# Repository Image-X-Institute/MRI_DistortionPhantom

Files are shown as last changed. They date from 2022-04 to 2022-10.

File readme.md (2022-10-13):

# MRI_DistortionPhantom


> :warning: this repo is archived; the most up to date documentaiton and code can be found [here](https://github.com/ACRF-Image-X-Institute/mri_distortion_toolkit)

This repository contains code to generate a customized MRI Distortion Phantom in [FreeCAD](https://www.freecadweb.org/). We also provide a 'how to' on manufacturing and imaging such a phantom in [our documentation](https://acrf-image-x-institute.github.io/MRI_DistortionPhantom/). For analysis of the phantom images, please see [this repository](https://github.com/ACRF-Image-X-Institute/MRI_DistortionQA)

Compared to other MRI distortion phantoms, this is:

- Free and open source
- Completely user customizable  
- Water free: light weight and leak free
- Designed for cheap and easy construction



## Setup/Build/Install

- Download and install [FreeCAD](https://www.freecadweb.org/). This work was tested with FreeCAD V0.19. The scripts will be executed within the FreeCAD python environment, so you don't need any additional libraries.
- Clone this repository

## Usage

- To generate your first phantom design, please see the [getting started](https://acrf-image-x-institute.github.io/MRI_DistortionPhantom/GettingStarted.html) page in the docs
- Important note: This code is <u>only</u> designed to worked from within FreeCAD. Any attempts to execute it from outside FreeCAD will fail.

## Directory Structure

- **docs** contains html documentation
- **docsrc** markdown/rst source documentation

## Acknowledgements 

This phantom design draws heavily on previous work undertaken at Ingham Institute/ Liverpool Cancer Center on MRI phantom development as described [here](https://aapm.onlinelibrary.wiley.com/doi/pdfdirect/10.1118/1.4915920?casa_token=CcBf93ylYfoAAAAA:yn6h_k-mTRJ2orijpwzfoUtX5zZchs-_qbcifwIP8X6oX2K19QKc7g7_oMXPMyspkzFAdUe-7rqEavzHzQ).

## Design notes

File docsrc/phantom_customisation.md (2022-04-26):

# Phantom Customization

The baseline model of a distortion phantom is highly customizable. You can change any of the parameters in the FoamProtoypeExample.py file. One of main reasons you may wish to do this is that different scanner have different field of views, so you may wish to make your phantom larger or smaller.
All options for the AddPhantomSlice class are described within the [code docs](), but we provide some additional notes on some of the more common things you may wish to change below:

## Specifying marker locations 

The marker locations are specified on each slice object. We provide two methods to automatically generate marker locations: ```HoleCentroids=cartesian``` will generate a cartesian grid of markers, while ```ROI_polar```  will generate concentric rings of markers. Both wil the ```hole_spacing``` parameter to space out markers. If you specify a ```DSV```,  the ```ROI_polar``` option will ensure good marker coverage over the surface of this sphere, and will provide an etch of the intersection of the DSV on each slice surface so you can tell where the DSV is on each slice.

You can specify a crosshair of markers using the ```ReferenceCrosshairRadius``` option. This will add a crosshair of markers within ```ReferenceCrosshairRadius```. This is a good idea to add to the central slice, as it makes alignment with CT/Ground truth much easier.

Finally, you may not wish to use any of the existing methods for defining marker positions. In that case, you are free to simply specify them as a list: ```HoleCentroids = [[x1,x2,x3],[y1,y2,y3]]```

## Specifying a load region

This phantom consists of a base material that does not give MRI signal, and is then packed with oil capsules, which also don't generate much signal. This can result in the RF coil of the scanner not being properly loaded. To avoid this, it is a good idea to add some load to your phantom. You can specify a region to be cut from the center of each slice using e.g. ```LoadRegion={'shape': 'rectangle', 'width': 100, 'height': 200}``` (see code docs for other options).

In our experience, not much load is required: during development we simple put a container of oil capsules into a zip lock bag. The exact location of the load also shouldn't be especially sensitive, just put it somewhere near the middle. 

## Specifying a DSV

Specifying a Diameter of Spherical Volume (DSV) has two effects

1. the intersection of the DSV with each slice will be etched on the surface of the slice
2. If you specify ```HoleCentroids=ROI_polar``` then the code will ensure good marker coverage over the surface of the DSV sphere. This can be important if you wish to fit spherical harmonics using this data.

## Specifying Guide Rods

This phantom is based on the concept of individual slices which are stacked on top of each other. A number of methods can be envisaged to hold all of these slices together, but internally we have been using nylon guide rods with great success. 

To specify guide rods, simply use ```GuideRods={'radius': 5, 'position': 30, 'height': 370}```. This will add four holes to the corner of your slice. Each hole will have a radius of` radius` and be  `position` mm from the edge of the slice.

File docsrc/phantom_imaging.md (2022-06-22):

# Phantom Imaging

Below are some things to think about when imaging the phantom. \

All our development work has been on a siemens scanner running VB 19A. Therefore, although the principles outlined below are scanner independent, the specific instructions are siemens specific. If you can update these instructions for other vendors, please do so! 

## Fat-Water chemical shift
If you use oil capsules as the markers in your phantom, there is an important effect you must be aware of: [Fat-Water chemical shift](https://mriquestions.com/f-w-chemical-shift.html). This means if your scanner has a center frequency calibrated for water (which it almost certainly does), the oil based capsules will be offset in the readout direction. There are a number of things you can do to avoid this:

1. **Set the scanner center frequency to oil instead of wate**r. Most scanners should have some method to reset the central frequency based on a given load. Specific instructions are scanner specific; an example from our siemens scanner is shown below.  The phantom itself may not provide sufficient load to carry out this procedure; in this case you could simply use a bottle of oil. If you successfully reset the central frequency, you will remove any offsets due to fat-water shift. The central frequency is encoded in the dicom header, so you can always retrospectively check what was used.
2. **Use a large bandwidth**: Since fundamentally this is a B0 distortion, the same mitigation used for B0 can be used. If you use a large enough bandwidth, the fat-water shift will be almost eliminated. However, this will also result in a drop in SNR, so the tradeoff must be made carefully. 
3. **Correct in software**: the fat-water shift is a known effect; its magnitude at a given field strength can easily be calculated. Therefore, it is in possible to [correct for it in software](https://acrf-image-x-institute.github.io/MRI_DistortionQA/code_docs.html#module-MRI_DistortionQA.MarkerAnalysis).
4. **Use water based markers:** In many ways this is the ideal solution, except for one thing: we haven't been able to find any water based markers yet!

In general, the best way to check whether you have removed the fat-water shift is to compare markers near the **center** of a phantom that were taken with a forward/reverse read out gradient (instructions for a siemens scanner below). Since B0 homogeneity should be good at the center of the phantom, if the central markers are not well aligned then it is because fat-water shift.

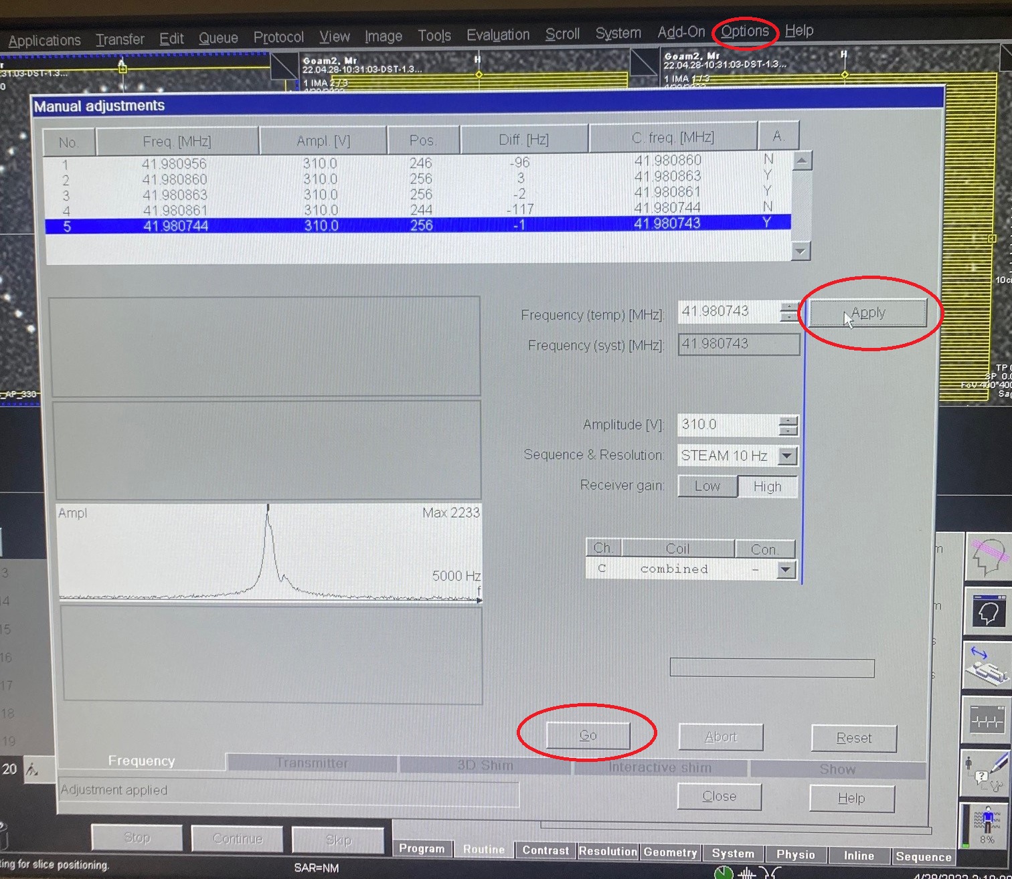
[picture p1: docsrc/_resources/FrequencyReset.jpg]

**Figure: for a siemens scanner, the center frequency can be reset for a given load by going options>>adjustments then clicking go until the measurement converges (may take a few tries). Then click apply to apply the new frequency.**

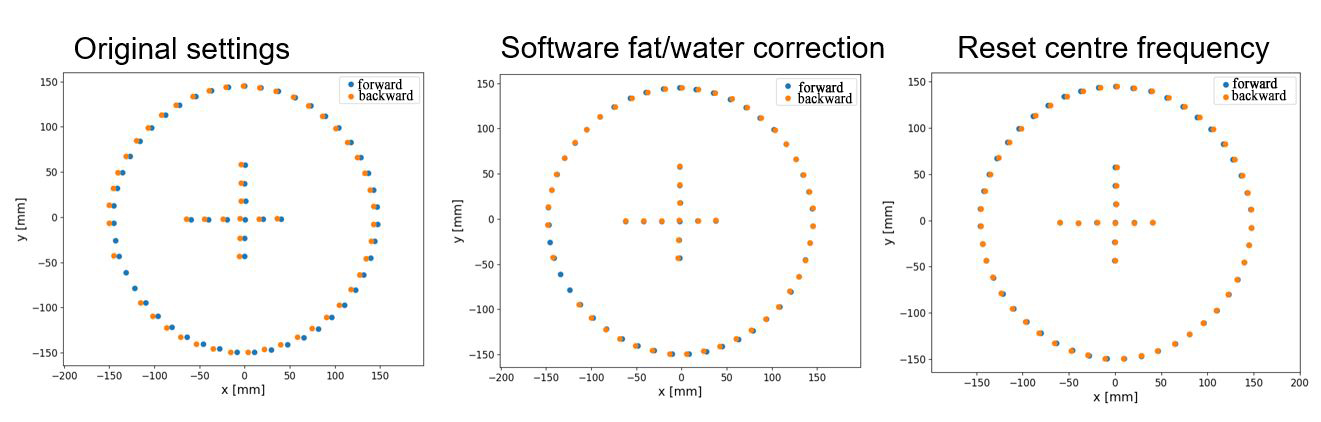
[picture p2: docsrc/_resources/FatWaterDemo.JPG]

**Figure: In the original image, no fat water correction has been made. As a result, the markers in the center of the image are offset from each other in the frequency direction. In the second image, this effect has been corrected for in software. In the third image, this effect has been corrected for by adjust the center frequency of the scanner.**

## Separation of B0/ Gradient distortion effects

There are two 'system based' sources of distortion in MRI: the gradient coils, and B0 inhomogeneity (there are also patient specific effects, which we ignore here.)

- Gradient distortion appears in every direction, and is essentially independent of imaging sequence.
- For standard sequences, B0 distortion appears only in the **readout** (frequency encode) direction, and is [highly sequence dependent](https://pubmed.ncbi.nlm.nih.gov/19810464/) . 

For a given sequence, these effects can be separated as follows: 

1. Take the first phantom image
2. Reverse the phase encoding direction. See image below for example in a siemens scanner.
3. The gradient distortion is the same in both images, while the direction of B0 distortion is reversed. Therefore, the gradient distortion is the average position of each marker between the two images.

To put this into a very simple example: consider just one marker and one dimension. This marker has a ground truth position (for instance measured with CT) of x_gt; gradient non-linearity causes it instead to appear at x_gnl. If we take two scans with opposite encoding directions x_forward and x_backward, we observe this marker at x_scan1 and x_scan2. We can separate the gradient and B0 effects as follows:
```
x_gnl = mean(x_scan1, x_scan2) = (x_scan1, x_scan2)/2
x_b0 = x_gt - x_gnl
```
At this point, we have a good estimate of the perturbation caused by gradient non-linearity in x which will be sequence independent, and a good estimate of the perturbation caused by B0, which will be sequence dependent. We would then have to repeat this process for encoding directions y and z to get a good estimate of each gradient field.

If this all makes your head hurt as much as it does mine, you have two options:

1. If you don't care about B0 (e.g. you are sure it is small enough that you don't need to worry about it), then use a large imaging bandwidth in conjunction with a spin echo sequence. Both of these will minimize your sensitivity to B0 inhomogeneity such that you can ignore B0 effects.
2. We have provide analysis software (**coming soon**!) ADD LINK that automates these steps for you. 

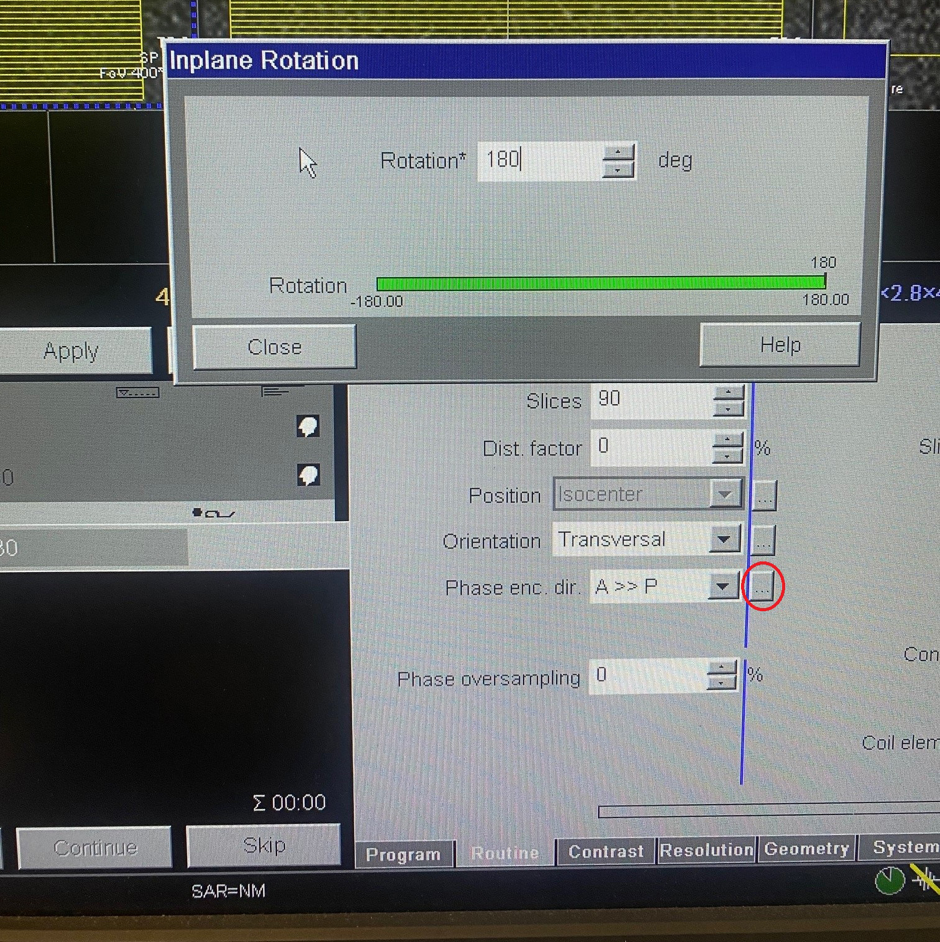
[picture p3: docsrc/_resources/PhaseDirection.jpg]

**Figure: this is the screen where you can reverse the phase encoding direction in the Siemens software. In the siemens software, reversing the phase encoding direction also reverses the read out (frequency) direction.**

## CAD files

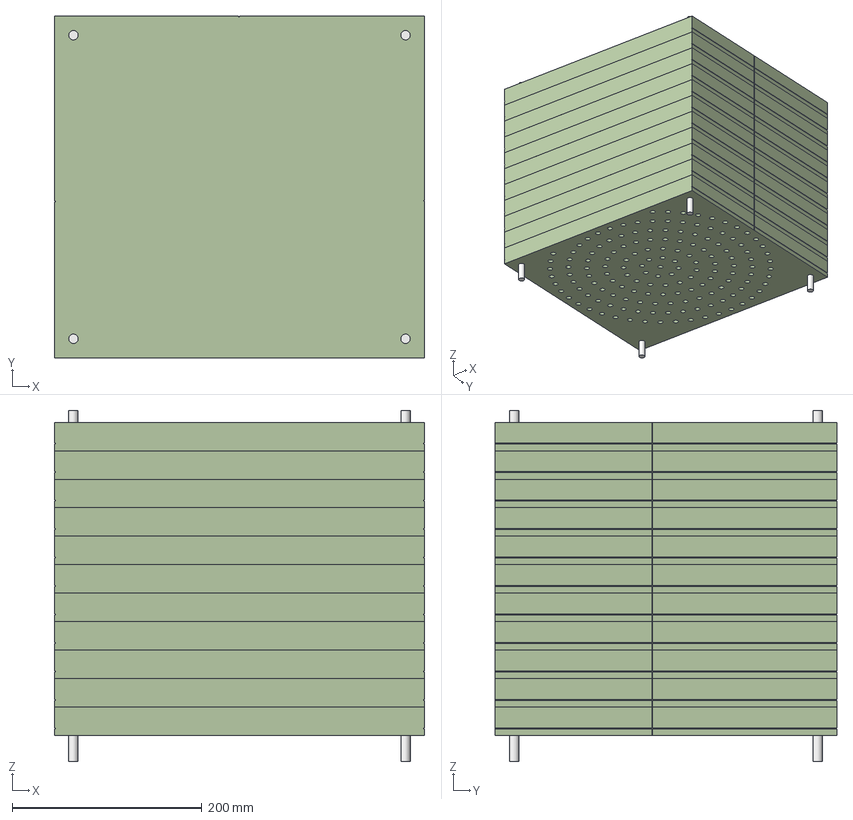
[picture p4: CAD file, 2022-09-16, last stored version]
phantom_drawings/EvolutionGearPhantom.FCStd
390.0 x 360.0 x 370.0 mm
Slice_z__150_0
Slice_z__120_0
Slice_z__90_0
Slice_z__60_0
Slice_z__30_0
Slice_z_0_0
Slice_z_30_0
Slice_z_60_0
Slice_z_90_0
Slice_z_120_0
Slice_z_150_0
DSV
Guide_TL011
Guide_TR011
Guide_BR011
Guide_BL011
combined_guides011

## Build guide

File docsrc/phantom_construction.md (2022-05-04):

# Phantom Construction

To a first order, the intention of this repository is to enable users to generate a CAD model of a distortion phantom; exactly how to construct it and what to construct it from is somewhat up to the user!

With that said, here are some notes about how we have gone about this previously.

## Specifying geometry for manufacture

When you build your phantom, each "Slice" object has a method called ```add_full_scale_drawing```. This does exactly what it sounds like: adds a 1:1 scale drawing of that slice into the FreeCAD object tree. To add a drawing of a slice, the code looks like the below.

````py
Slice = PhantomBuilder.AddPhantomSlice()
Slice.add_full_scale_drawing()
````

In the FoamPrototypeExample we provide, you would have to add the add_full_scale_drawing() call to eace slice in the for loop.

To export each drawing, simply select it, click file, export, then export as pdf.

From here, you can either print out each pdf if you intend to construct a phantom manually, or send this directly to the manufacturer. In our experience, this pdf drawing along with a phone call were all manufacturers needed.

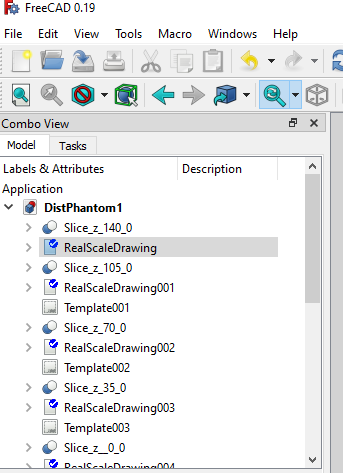
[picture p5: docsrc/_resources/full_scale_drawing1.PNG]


**Figure: using the full_scale_drawing** adds multiple drawings into the Model tree. Each of these must be manually exported (for now. we will add an auto method in future)

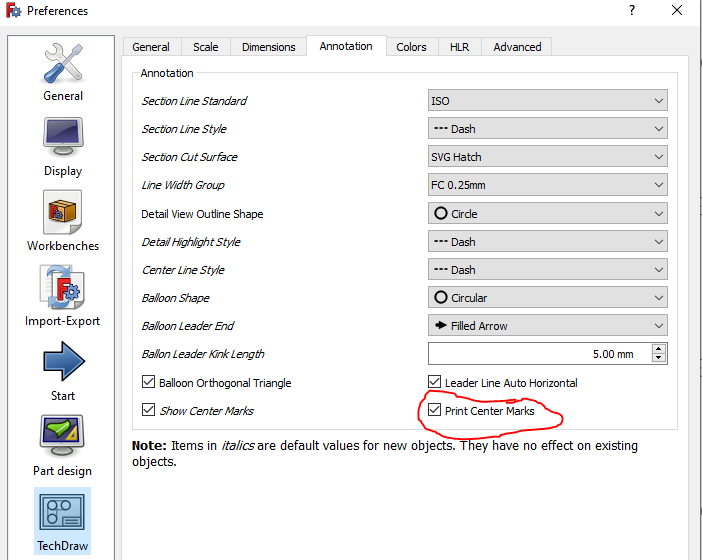
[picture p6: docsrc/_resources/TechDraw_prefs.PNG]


**Figure: we suggest enabling the 'Print Center Marks' option, which doesn't show up in FreeCAD but will print a crosshair in each circle when you export to pdf. This is especially important if you intend to manually drill the holes**

## Markers

The phantom has a number of holes to put markers in, but what should you actually use for markers? We have had a lot of success using fish oil capsules such as [these](https://www.blackmores.com.au/products/fish-oil-1000). Note that the use of oil has ramifications for MRI imaging; we discuss these and provide [suggestions on how to take images safely](https://acrf-image-x-institute.github.io/MRI_DistortionPhantom/phantom_imaging.html)

## Background material

The slice could be constructed of anything MRI neutral. We have constructed phantoms from [blue foam](https://dctech.com.au/products/styrofoam-rtm-x/) and [add type of foam](https://www.evolutiongear.com.au/custom-foam-cutting/). If you can find a robust way to manufacture it, foam is an excellent choice as it is super lightweight and storng. However, as described below it can be difficult to manufacture. Alternatively you could use a lightweight plastic but note that even 'light' plastic tends to get quite heavy!

## Joining the slices together

To join the slices together, we used [threaded nylon guide rods](https://www.unitedfasteners.com.au/products/fasteners-fixings/nylon/threaded-rod/nylon-threaded-rod), [washers](https://www.unitedfasteners.com.au/products/fasteners-fixings/nylon/washers/nylon-flat-round-standard-washer) and [nuts](https://www.unitedfasteners.com.au/products/fasteners-fixings/nylon/nuts/nylon-wing-nut). One could also imagine for instance a specialized 'slice holder' like a box that all the slices could slot into, but we did not explore this. 

## Before your first prototype: general tips

- Getting the holes the right size for the markers can involve some trial and error. It's a good idea to build a few single slice prototypes before continuing to a full design. 

## First prototype: Drill press

For our first phantom, we used a drill press on  [blue foam](https://dctech.com.au/products/styrofoam-rtm-x/). An image of this is below. This was quite sucessful, but rather painful to construct a phantom with many holes drilled. There are also obvious limitations to the accuracy of hole placement. We also found that unless you have a high quality drill press, the foam is quite prone to crumbling. 

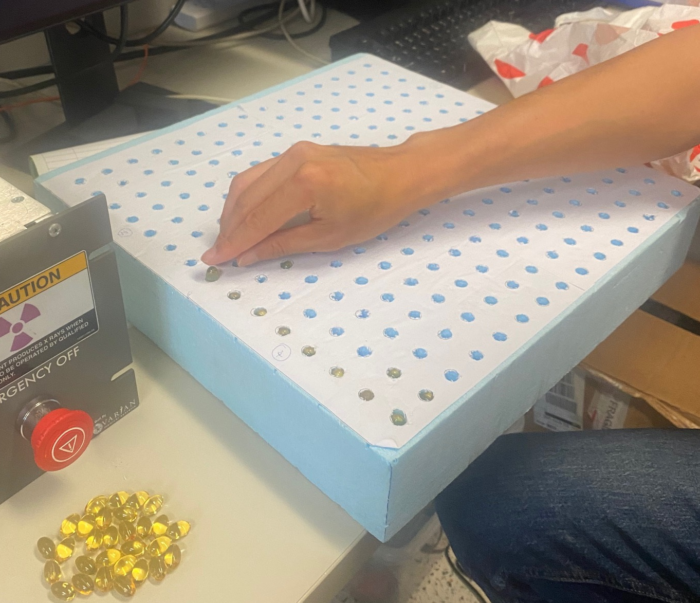
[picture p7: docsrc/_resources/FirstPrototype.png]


**Figure: Action shot of our first slice prototype in action!**

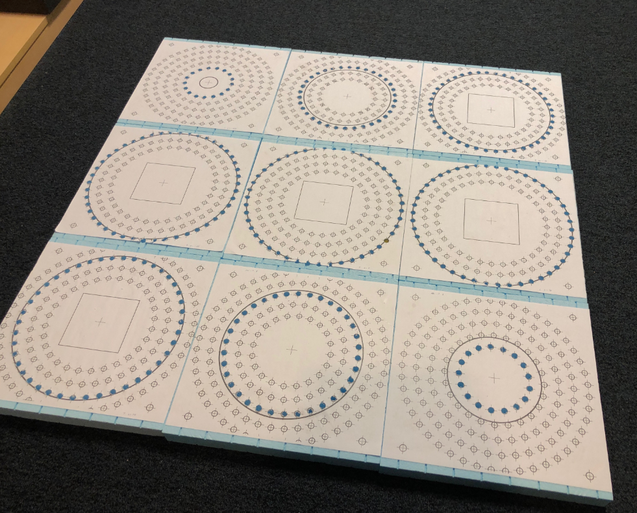
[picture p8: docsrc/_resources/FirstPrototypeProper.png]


**Figure: all slices from a drill press based phantom**

## Second protoype: Laser cut foam

The drill press version was excellent for development, but long term we wanted something more accurate and less labor intensive. For our second prototype, we utilized laser cut foam. There are many vendors capable of this manufacturing technique; we worked with [evolution gear](https://www.evolutiongear.com.au/custom-foam-cutting/). 

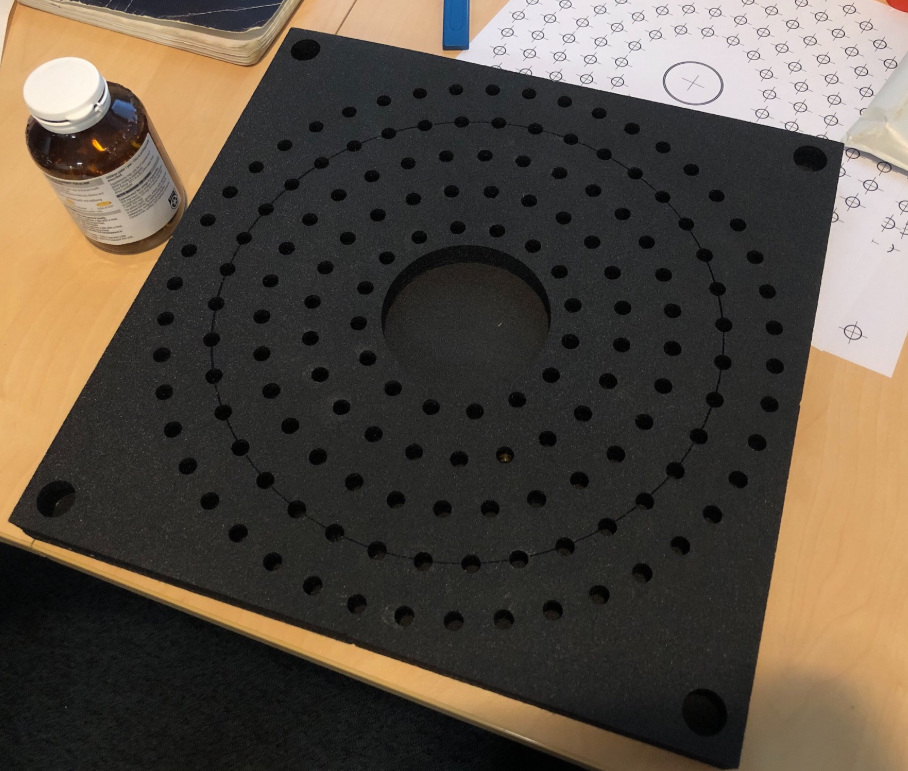
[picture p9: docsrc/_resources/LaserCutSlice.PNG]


**Figure: slice from a laser cut foam provider**

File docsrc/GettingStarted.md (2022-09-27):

# Getting Started

## Setting up FreeCAD

FreeCAD of course has its [own documentation](https://wiki.freecad.org/Getting_started), which should be your first point of call for any trouble shooting of this program. Here, we provide a basic intro into setting up and configuring freeCAD so that you can build your first phantom. 

1. [Download FreeCAD](https://www.freecadweb.org/downloads.php). This code was developed and tested with version 0.19. Future versions should work, but if you run into issues go with version 0.19
2. Open FreeCAD 
3. In “View” “panels” enable both the python console and the report view. This isn't required, but in my opinion tends to make life easier!
4. After these steps, you should have something that looks like the image below, and are ready to generate your first phantom!

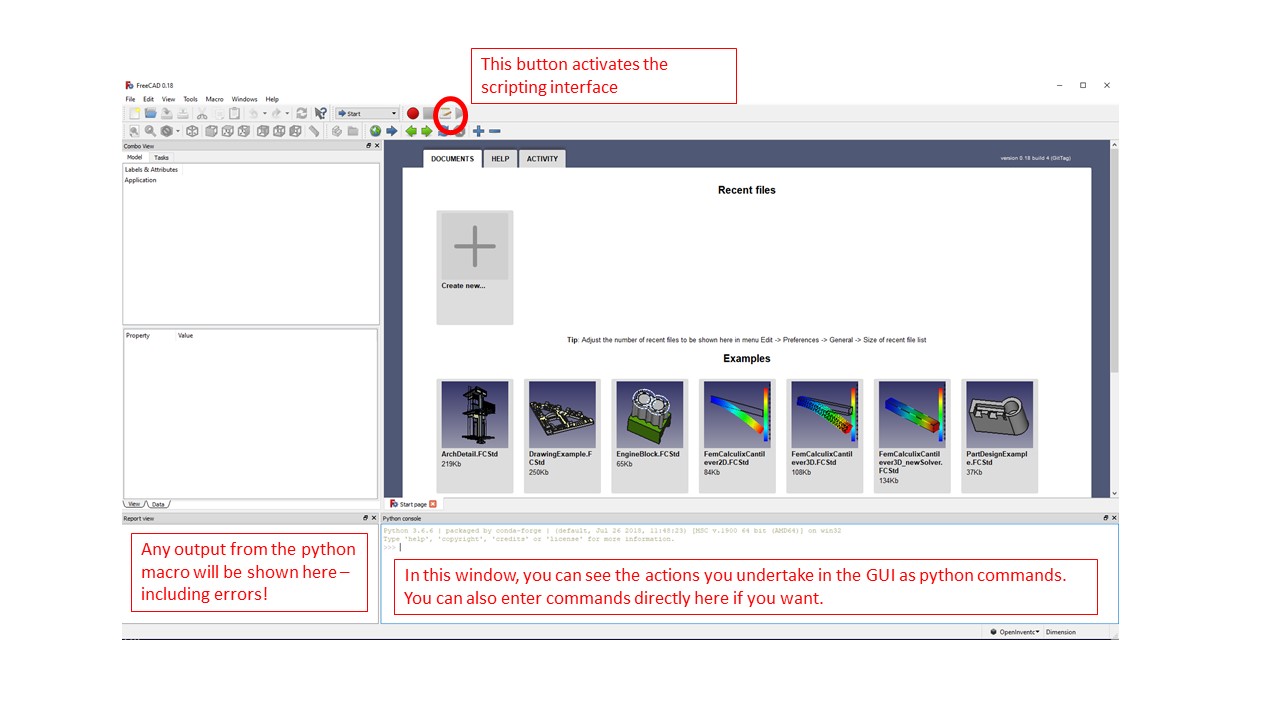
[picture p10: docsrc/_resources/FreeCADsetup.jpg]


## Generating your first phantom design

1. Open the scripting interface using the button in the top right in the figure above (or through the menus, click macro, macros)
2. Navigate to wherever you cloned [this repository](https://github.com/ACRF-Image-X-Institute/MRI_DistortionPhantom) and choose the phantom_designs folder
3. Execute phantom_template.py as a macro (or any of the other designs)
4. That's it! you can open up the  FoamPrototypeExample.py script to see exactly what it's doing, and you can read the section on [customizing the phantom](https://acrf-image-x-institute.github.io/MRI_DistortionPhantom/phantom_customisation.html#) to change this basic design to your hearts desire.

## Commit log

2022-06-16 new design for evolution gear. fixes #10
2022-06-16 this is the version sent to evolution gear
    [EvolutionGearPhantom.FCStd]
2022-09-27 tidying up structure, adding back in elipse slice base, and adding examples of different geometries
    [EvolutionGearPhantom.FCStd]
2022-09-28 Update Evolution gear design. increased hole thickness again. made load region only on side it makes sense
2022-09-28 reduced hole size from 8.7/2 to 8.5/2
